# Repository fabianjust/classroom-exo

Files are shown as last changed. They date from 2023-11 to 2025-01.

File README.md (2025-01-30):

# classroom-exo
Classroom-ready open-source educational exoskeleton for biomedical and control engineering

The classroom Exo development is guided by the manual.
The manual is designed to assist you in seamlessly transitioning from EduExoPro to Classroom Exo. Whether you're a developer, educator, or enthusiast, the detailed content in each folder aims to provide clarity and guidance.

How to Use This Manual:
Begin by reading through the manual to familiarize yourself with the upgrade process.
Depending on your area of interest or expertise, navigate to the specific folders that match your requirements—whether it's CAD, PCB design, electronics, or material lists.
Feel free to collaborate by providing feedback, raising issues, or contributing to the ongoing development of Classroom Exo. Your input is highly valued.

We prepared three lab instructions for a) Force Control, b) Muscle Activity Control, and c) PID Control for Biomedical and Control Engineering University Education. Feel free to use these documents to build your own lab for a physical human-machine interaction, health robotics, and for all control theory courses.

If you want to know more about the Classroom Exo, check out the corresponding Journal Paper: https://www.degruyter.com/document/doi/10.1515/auto-2023-0208/html

We hope this manual serves as a valuable resource in your journey to implement Classroom Exo. 
Happy exploring and building with Classroom Exo!

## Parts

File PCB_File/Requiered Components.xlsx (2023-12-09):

Reference | Value | MPN | Qty/unit | LINK | Column1
> R2-R4 | 10k | RC0805JR-0710KL | 3 | LINK (https://www.digikey.se/en/products/detail/yageo/RC0805JR-0710KL/728241)
R13 | 300R | RC0805JR-07300RL | 1 | LINK (https://www.digikey.se/en/products/detail/yageo/RC0805JR-07300RL/728307?s=N4IgTCBcDaIEoGEAMAOJBWAUnAtEg7AMxJJwAyIAugL5A)
R1 | 60.4R | RC0805FR-0760R4L | 1 | LINK (https://www.digikey.se/en/products/detail/yageo/RC0805FR-0760R4L/728073)
R11 | 5.24k | RC0805FR-075K23L | 1 | LINK (https://www.digikey.se/en/products/detail/yageo/RC0805FR-075K23L/727993)
R12 | 30.31k | RC0805FR-0730K1L | 1 | LINK (https://www.digikey.se/en/products/detail/yageo/RC0805FR-0730K1L/727845)
> R6, R7 | 100k | RC0805FR-13100KL | 2 | LINK (https://www.digikey.se/en/products/detail/yageo/RC0805FR-13100KL/13694147?s=N4IgTCBcDaIEoGEAMAOJBWAYnAtARgGY8kkBpAGRAF0BfIA)
R8 | 383R | RC0805FR-07383RL | 1 | LINK (https://www.digikey.se/en/products/detail/yageo/RC0805FR-07383RL/727896?s=N4IgTCBcDaIEoGEAMAOJBWAYnAtEg7AMwqFwAyIAugL5A)
R14 | 170R | RC0805FR-07174RL | 1 | LINK (https://www.digikey.se/en/products/detail/yageo/RC0805FR-07174RL/727639)
D3 | LED_RED | LTST-C191KRKT | 1 | LINK (https://www.digikey.se/en/products/detail/liteon/LTST-C191KRKT/386837?s=N4IgTCBcDaIDIBUDKCC0BhAjATkwaQCU8EQBdAXyA)
D2 | LED_Blue | LTST-C191TBKT | 1 | LINK (https://www.digikey.se/en/products/detail/liteon/LTST-C191TBKT/388530)
> D5, D6 | ESD321 | ESD321DPYR | 2 | LINK (https://www.digikey.se/en/products/detail/texas-instruments/ESD321DPYR/9559035?s=N4IgTCBcDaIKIGUAiBmMBGJAFAmgJRAF0BfIA)
D4 | D1213A | D1213A-01WS-7 | 1 | LINK (https://www.digikey.se/en/products/detail/diodes-incorporated/D1213A-01WS-7/3340446?s=N4IgTCBcDaICIEYwIMwEEC0AGBB1AyhgOwgC6AvkA)
C2 | 6.8uF | C2012X8L0J685K125AC | 1 | LINK (https://www.digikey.se/en/products/detail/tdk-corporation/C2012X8L0J685K125AC/8343788)
C4 | 47nF | C2012X7T2W473K125AA | 1 | LINK (https://www.digikey.se/en/products/detail/tdk-corporation/C2012X7T2W473K125AA/2733189)
> C9, C10, C12, C14, C17 | 100nF | C2012X7R2A104K125AA | 5 | LINK (https://www.digikey.se/en/products/detail/tdk-corporation/C2012X7R2A104K125AA/569044?s=N4IgTCBcDaIMJgAwEYwA0DsAlMBBZiALANKoCsuuIAugL5A)
> C1, C11, C13, C15, C18 | 1uF | C2012X7R1H105K125AB | 5 | LINK (https://www.digikey.se/en/products/detail/tdk-corporation/C2012X7R1H105K125AB/2732982)
> C7, C8 | 22uF | C2012X5R1V226M125AC | 2 | LINK (https://www.digikey.se/en/products/detail/tdk-corporation/C2012X5R1V226M125AC/3951664?s=N4IgTCBcDaIMJgAwEYwA0CsAlZA1MYAbALKoYCCcIAugL5A)
C5 | 4.7uF | C2012X5R1E475K125AB | 1 | LINK (https://www.digikey.se/en/products/detail/tdk-corporation/C2012X5R1E475K125AB/1986842)
> C3, C6, C16 | 10uF | C2012X5R1E106K125AB | 3 | LINK (https://www.digikey.se/en/products/detail/tdk-corporation/C2012X5R1E106K125AB/2443462)
D1 | BAT60B | BAT60BE6327HTSA1 | 1 | LINK (https://www.digikey.se/en/products/detail/infineon-technologies/BAT60BE6327HTSA1/1280935)
J5 | USB_B_Micro | 10118192-0002LF | 1 | LINK (https://www.digikey.se/en/products/detail/amphenol-cs-fci/10118192-0002LF/6817756?s=N4IgTCBcDaIIwAY5wBxwJxgLQN2AMgGIgC6AvkA)
J4 | SRV0 | 1-2834011-4 | 1 | LINK (https://www.digikey.se/en/products/detail/te-connectivity-amp-connectors/1-2834011-4/5872966?s=N4IgTCBcDaIIwFowA4DMAWADHR6QF0BfIA)
J3 | SG0 | 1-2834011-4 | 1 | LINK (https://www.digikey.se/en/products/detail/te-connectivity-amp-connectors/1-2834011-4/5872966?s=N4IgTCBcDaIIwFowA4DMAWADHR6QF0BfIA)
J2 | EMG1 | 1-2834011-3 | 1 | LINK (https://www.digikey.se/en/products/detail/te-connectivity-amp-connectors/1-2834011-3/5872965?s=N4IgTCBcDaIIwFowA4DMAWADHRqQF0BfIA)
J1 | EMG0 | 1-2834011-3 | 1 | LINK (https://www.digikey.se/en/products/detail/te-connectivity-amp-connectors/1-2834011-3/5872965?s=N4IgTCBcDaIIwFowA4DMAWADHRqQF0BfIA)
J6 | BAT0 | 1-2834011-2 | 1 | LINK (https://www.digikey.se/en/products/detail/te-connectivity-amp-connectors/1-2834011-2/5872964?s=N4IgTCBcDaIIwFowA4DMAWADHREC6AvkA)
L1 | 1uH | 0630CDMCCDS-1R5MC | 1 | LINK (https://www.digikey.se/en/products/detail/sumida-america-inc/0630CDMCCDS-1R5MC/5812455)
U3 (RGBSwitch) | LP11EE1NCSRGB | LP11EE1NCSRGB | 1 | LINK (https://www.digikey.se/en/products/detail/e-switch/LP11EE1NCSRGB/9771933?s=N4IgTCBcDaIDIAUCMSCiqkDkDCBlASgOIBCIAugL5A)
U2 (BatteryManagment) | BQ25886RGER | BQ25886RGER | 1 | LINK (https://www.digikey.se/en/products/detail/texas-instruments/BQ25886RGER/10273215?s=N4IgTCBcDaIEIEUwFYAcqBsAlA4gUSxAF0BfIA)
U1 (Amplifier) | INA125P | INA125P | 3 | LINK (https://www.digikey.se/en/products/detail/texas-instruments/INA125P/254670)
U1 (Socket) | INA125P | ICM-316-1-GT-HT | 3 | LINK (https://www.digikey.se/en/products/detail/adam-tech/ICM-316-1-GT-HT/9833008?s=N4IgTCBcDaIJIGECyBaAzARgGwoyg4gCooAShIAugL5A)
R10 | Iset (5.7k) | RC0805FR-075K76L | 1 | LINK (https://www.digikey.se/en/products/detail/yageo/RC0805FR-075K76L/728007)
R9 | Vset(150k) | RC0805FR-07150KL | 1 | LINK (https://www.digikey.se/en/products/detail/yageo/RC0805FR-07150KL/727614)
Q2 | Si3483CDV | SI3483CDV-T1-GE3 | 1 | LINK (https://www.digikey.se/en/products/detail/vishay-siliconix/SI3483CDV-T1-GE3/2441608)
Q1 | BSS123 | BSS123 | 1 | LINK (https://www.digikey.se/en/products/detail/anbon-semiconductor-int-l-limited/BSS123/16708487)
A1 | Arduino_Nano_33_IOT | PPPC101LFBN-RC (10P) | 2 | LINK (https://www.digikey.se/en/products/detail/sullins-connector-solutions/PPPC101LFBN-RC/810182?s=N4IgTCBcDaIAoIMIEYAMyAyAxAQgOQFoAlREAXQF8g)
A1 | Arduino_Nano_33_IOT | PPPC051LFBN-RC (5P) | 2 | LINK (https://www.digikey.se/en/products/detail/sullins-connector-solutions/PPPC051LFBN-RC/810177?s=N4IgTCBcDaIAoIMIAYCsBGAMgMQEIDkBaAJURAF0BfIA)
PWR_TP | TestPoint (White) | 5000 | 6 | LINK (https://www.digikey.se/en/products/detail/keystone-electronics/5000/255326)
SRV0_TP | TestPoint (Yellow) | 5004 | 4 | LINK (https://www.digikey.se/en/products/detail/keystone-electronics/5004/362669)
> EMG0, EMG1_TP | TestPoint (Orange) | 5003 | 2 | LINK (https://www.digikey.se/en/products/detail/keystone-electronics/5003/362668)
> GND_TP | TestPoint (Black) | 5001 | 4 | LINK (https://www.digikey.se/en/products/detail/keystone-electronics/5001/255327)
SG0_TP | TestPoint (White) | 5002 | 3 | LINK (https://www.digikey.se/en/products/detail/keystone-electronics/5002/255328)
Myoware Cable | Myoware Cable | CAB-12970 | 2 | LINK (https://www.digikey.se/sv/products/detail/sparkfun-electronics/CAB-12970/6833933?productid=6833933)
Myoware Cable Shield | Myoware Cable Shield | Myoware Cable Shield | 2 | LINK (https://www.fruugo.se/replacement-wearable-for-myoware-cable-shield-muscle-sensor-module-board/p-118668884-249379639?language=en&ac=ProductCasterAPI&asc=pmax)
Screw thread Insert M3 |  | K0978.03 | 15 | Link (https://uk.misumi-ec.com/vona2/detail/221303964730/?HissuCode=K0978.03)
Screw thread Insert M4 |  | K0978.04 | 15 | link (https://uk.misumi-ec.com/vona2/detail/221303964730/?HissuCode=K0978.04)
Screw M3 |  | S3-6-P | 15 | Link (https://uk.misumi-ec.com/vona2/detail/221005514842/?HissuCode=S3-6-P)
Screw M4 |  | S4-45-P | 15 | link (https://uk.misumi-ec.com/vona2/detail/221005514842/?HissuCode=S4-45-P)
Battery | 7.4V/8.4V | CL-LP503759-2S1P |  | Link (https://www.batteriexperten.com/sv/artiklar/li-po-2s-74v-30c-1300mah-jst-rcy-bec-kontakt-vapex.html)
Soldering | NC191LT10 | NC191LT10
SRA NO CLEAN PASTE FLUX | FLS135NC | FLS135NC
 |  |  |  |  |  | # The quantities provided in this list represent the minimum requirement. We strongly recommend acquiring a surplus of components beyond the specified quantities for added flexibility and contingencies.

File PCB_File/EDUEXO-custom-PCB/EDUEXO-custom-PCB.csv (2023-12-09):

Source: | C:\Users\Mohammed Al-Tashi\Desktop\EXO V2\PCB_Designs\EDUEXO-custom-PCB\EDUEXO-custom-PCB.kicad_sch
Date: | 5/17/2023 20:34
Tool: | Eeschema (6.0.5)
Generator: | C:\Program Files\KiCad\6.0\bin\scripting\plugins/bom_csv_grouped_by_value.py
Component Count: | 74
Individual Components:
Item | Qty | Reference(s) | Value | LibPart | Footprint | Datasheet | MPN | config
 |  | +3V3 | TestPoint | Connector:TestPoint | TestPoint:TestPoint_Keystone_5000-5004_Miniature | https://www.keyelco.com/userAssets/file/M65p56.pdf | 5002
 |  | +5V0 | TestPoint | Connector:TestPoint | TestPoint:TestPoint_Keystone_5000-5004_Miniature | https://www.keyelco.com/userAssets/file/M65p56.pdf | 5002
 |  | A1 | Arduino_Nano_33_IOT | EDUEXO-custom-PCB:Arduino_Nano_33_IOT | EDUEXO-custom-PCB:MODULE_ABX00027_ThroughHoles | https://docs.arduino.cc/resources/datasheets/ABX00027-datasheet.pdf
 |  | ANGLE_SRV0 | TestPoint | Connector:TestPoint | TestPoint:TestPoint_Keystone_5000-5004_Miniature | https://www.keyelco.com/userAssets/file/M65p56.pdf | 5002
 |  | ARDu_CONTROL_SRV0 | TestPoint | Connector:TestPoint | TestPoint:TestPoint_Keystone_5000-5004_Miniature | https://www.keyelco.com/userAssets/file/M65p56.pdf | 5002
 |  | BAT_VALUE_0 | TestPoint | Connector:TestPoint | TestPoint:TestPoint_Keystone_5000-5004_Miniature | https://www.keyelco.com/userAssets/file/M65p56.pdf | 5002
 |  | C1 | 1uF | Device:C | Capacitor_SMD:C_0805_2012Metric | https://product.tdk.com/en/system/files | C2012X7R1H105K125AB
 |  | C2 | 6.8uF | Device:C | Capacitor_SMD:C_0805_2012Metric | https://product.tdk.com/en/system/files | C2012X8L0J685K125AC
 |  | C3 | 10uF | Device:C | Capacitor_SMD:C_0805_2012Metric | https://product.tdk.com/system/files/dam/doc/product/capacitor/ceramic/mlcc/catalog/mlcc_commercial_general_en.pdf | C2012X5R1E106K125AB
 |  | C4 | 47nF | Device:C | Capacitor_SMD:C_0805_2012Metric | https://product.tdk.com/en/system/files | C2012X7T2W473K125AA
 |  | C5 | 4.7uF | Device:C | Capacitor_SMD:C_0805_2012Metric | https://product.tdk.com/system/files/dam/doc/product/capacitor/ceramic/mlcc/catalog/mlcc_commercial_general_en.pdf | C2012X5R1E475K125AB
 |  | C6 | 10uF | Device:C | Capacitor_SMD:C_0805_2012Metric | https://product.tdk.com/system/files/dam/doc/product/capacitor/ceramic/mlcc/catalog/mlcc_commercial_general_en.pdf | C2012X5R1E106K125AB
 |  | C7 | 22uF | Device:C | Capacitor_SMD:C_0805_2012Metric | https://product.tdk.com/system/files/dam/doc/product/capacitor/ceramic/mlcc/catalog/mlcc_commercial_general_en.pdf | C2012X5R1V226M125AC
 |  | C8 | 22uF | Device:C | Capacitor_SMD:C_0805_2012Metric | https://product.tdk.com/system/files/dam/doc/product/capacitor/ceramic/mlcc/catalog/mlcc_commercial_general_en.pdf | C2012X5R1V226M125AC
 |  | C9 | 100nF | Device:C | Capacitor_SMD:C_0805_2012Metric | https://product.tdk.com/en/system/files | C2012X7R2A104K125AA
 |  | C10 | 100nF | Device:C | Capacitor_SMD:C_0805_2012Metric | https://product.tdk.com/en/system/files | C2012X7R2A104K125AA
 |  | C11 | 1uF | Device:C | Capacitor_SMD:C_0805_2012Metric | https://product.tdk.com/en/system/files | C2012X7R1H105K125AB
 |  | C12 | 100nF | Device:C | Capacitor_SMD:C_0805_2012Metric | https://product.tdk.com/en/system/files | C2012X7R2A104K125AA
 |  | C13 | 1uF | Device:C | Capacitor_SMD:C_0805_2012Metric | https://product.tdk.com/en/system/files | C2012X7R1H105K125AB
 |  | C14 | 100nF | Device:C | Capacitor_SMD:C_0805_2012Metric | https://product.tdk.com/en/system/files | C2012X7R2A104K125AA
 |  | C15 | 1uF | Device:C | Capacitor_SMD:C_0805_2012Metric | https://product.tdk.com/en/system/files | C2012X7R1H105K125AB
 |  | C16 | 10uF | Device:C | Capacitor_SMD:C_0805_2012Metric | https://product.tdk.com/system/files/dam/doc/product/capacitor/ceramic/mlcc/catalog/mlcc_commercial_general_en.pdf | C2012X5R1E106K125AB
 |  | C17 | 100nF | Device:C | Capacitor_SMD:C_0805_2012Metric | https://product.tdk.com/en/system/files | C2012X7R2A104K125AA
 |  | C18 | 1uF | Device:C | Capacitor_SMD:C_0805_2012Metric | https://product.tdk.com/en/system/files | C2012X7R1H105K125AB
 |  | D1 | BAT60B | Device:D_Schottky | Diode_SMD:D_SOD-323 | https://www.infineon.com/dgdl/bat60bseries.pdf?folderId=db3a304313d846880113def5812204a1&fileId=db3a304314dca3890115195908c50f0b | BAT60BE6327HTSA1
 |  | D2 | LED_Blue | Device:LED | LED_SMD:LED_0603_1608Metric | https://optoelectronics.liteon.com/upload/download/DS22-2000-230/LTST-C191TBKT.pdf | LTST-C191TBKT
 |  | D3 | LED_RED | Device:LED | LED_SMD:LED_0603_1608Metric | https://optoelectronics.liteon.com/upload/download/DS22-2000-223/LTST-C191KRKT.PDF | LTST-C191KRKT
 |  | D4 | D1213A | Device:D_Zener | Diode_SMD:D_SOD-323 | https://www.diodes.com/assets/Datasheets/D1213A-01WS.pdf | D1213A-01WS-7
 |  | D5 | ESD321 | Diode:ESD9B3.3ST5G | Diode_SMD:D_0402_1005Metric | https://www.ti.com/lit/ds/symlink/esd321.pdf?HQS=dis-dk-null-digikeymode-dsf-pf-null-wwe&ts=1683194956063 | ESD321DPYR
 |  | D6 | ESD321 | Diode:ESD9B3.3ST5G | Diode_SMD:D_0402_1005Metric | https://www.ti.com/lit/ds/symlink/esd321.pdf?HQS=dis-dk-null-digikeymode-dsf-pf-null-wwe&ts=1683194956063 | ESD321DPYR
 |  | DRIVE_PWM_SRV0 | TestPoint | Connector:TestPoint | TestPoint:TestPoint_Keystone_5000-5004_Miniature | https://www.keyelco.com/userAssets/file/M65p56.pdf | 5002
 |  | EMG0 | TestPoint | Connector:TestPoint | TestPoint:TestPoint_Keystone_5000-5004_Miniature | https://www.keyelco.com/userAssets/file/M65p56.pdf | 5002
 |  | EMG1 | TestPoint | Connector:TestPoint | TestPoint:TestPoint_Keystone_5000-5004_Miniature | https://www.keyelco.com/userAssets/file/M65p56.pdf | 5002
 |  | GND1 | TestPoint | Connector:TestPoint | TestPoint:TestPoint_Keystone_5000-5004_Miniature | https://www.keyelco.com/userAssets/file/M65p56.pdf | 5002
 |  | GND2 | TestPoint | Connector:TestPoint | TestPoint:TestPoint_Keystone_5000-5004_Miniature | https://www.keyelco.com/userAssets/file/M65p56.pdf | 5002
 |  | GND3 | TestPoint | Connector:TestPoint | TestPoint:TestPoint_Keystone_5000-5004_Miniature | https://www.keyelco.com/userAssets/file/M65p56.pdf | 5002
 |  | GND4 | TestPoint | Connector:TestPoint | TestPoint:TestPoint_Keystone_5000-5004_Miniature | https://www.keyelco.com/userAssets/file/M65p56.pdf | 5002
 |  | H1 | M3 | Mechanical:MountingHole | MountingHole:MountingHole_3.2mm_M3 | ~
 |  | H2 | M3 | Mechanical:MountingHole | MountingHole:MountingHole_3.2mm_M3 | ~
 |  | H3 | M3 | Mechanical:MountingHole | MountingHole:MountingHole_3.2mm_M3 | ~
 |  | H4 | M3 | Mechanical:MountingHole | MountingHole:MountingHole_3.2mm_M3 | ~
 |  | J1 | EMG0 | Connector:Screw_Terminal_01x03 | EDUEXO-custom-PCB:TE_1-2834011-3 | https://www.te.com/commerce/DocumentDelivery/DDEController?Action=srchrtrv&DocNm=1-1773872-7_ModularScrewlessTerminalBloc&DocType=DS&DocLang=English | 1-2834011-3
 |  | J2 | EMG1 | Connector:Screw_Terminal_01x03 | EDUEXO-custom-PCB:TE_1-2834011-3 | https://www.te.com/commerce/DocumentDelivery/DDEController?Action=srchrtrv&DocNm=1-1773872-7_ModularScrewlessTerminalBloc&DocType=DS&DocLang=English | 1-2834011-3
 |  | J3 | SG0 | Connector:Screw_Terminal_01x04 | EDUEXO-custom-PCB:TE_1-2834011-4 | https://www.te.com/commerce/DocumentDelivery/DDEController?Action=srchrtrv&DocNm=1-1773872-7_ModularScrewlessTerminalBloc&DocType=DS&DocLang=English | 1-2834011-4
 |  | J4 | SRV0 | Connector:Screw_Terminal_01x04 | EDUEXO-custom-PCB:TE_1-2834011-4 | https://www.te.com/commerce/DocumentDelivery/DDEController?Action=srchrtrv&DocNm=2834011&DocType=Customer+Drawing&DocLang=English | 1-2834011-4
 |  | J5 | USB_B_Micro | EDUEXO-custom-PCB:USB_B_Micro | EDUEXO-custom-PCB:USB_micro_B_10118192-0002LF | https://www.amphenol-cs.com/media/wysiwyg/files/drawing/10118192.pdf | 10118192-0002LF
 |  | J6 | BAT0 | Connector:Screw_Terminal_01x02 | EDUEXO-custom-PCB:TE_1-2834011-2 | https://www.te.com/commerce/DocumentDelivery/DDEController?Action=srchrtrv&DocNm=2834011&DocType=Customer+Drawing&DocLang=English | 1-2834011-2
 |  | L1 | 1uH | pspice:INDUCTOR | EDUEXO-custom-PCB:L_0630CDMCCDS-1R5MC | https://products.sumida.com/products/pdf/0630CDMCCDS.pdf?t=1611592302 | 0630CDMCCDS-1R5MC
 |  | OUTPUT_SG0 | TestPoint | Connector:TestPoint | TestPoint:TestPoint_Keystone_5000-5004_Miniature | https://www.keyelco.com/userAssets/file/M65p56.pdf | 5002
 |  | POWER_SRV0 | TestPoint | Connector:TestPoint | TestPoint:TestPoint_Keystone_5000-5004_Miniature | https://www.keyelco.com/userAssets/file/M65p56.pdf | 5002
 |  | Q1 | BSS123 | Transistor_FET:BSS123 | Package_TO_SOT_SMD:SOT-23 | http://www.diodes.com/assets/Datasheets/ds30366.pdf
 |  | Q2 | Si3483CDV | EDUEXO-custom-PCB:Si3483CDV | Package_TO_SOT_SMD:TSOT-23-6 | https://www.vishay.com/docs/68603/si3483cd.pdf
 |  | R1 | 60.4R | Device:R | Resistor_SMD:R_0805_2012Metric | https://www.yageo.com/upload/media/product/productsearch/datasheet/rchip/PYu-RC_Group_51_RoHS_L_12.pdf | RC0805FR-0760R4L
 |  | R2 | 10k | Device:R | Resistor_SMD:R_0805_2012Metric | https://www.yageo.com/upload/media/product/productsearch/datasheet/rchip/PYu-RC_Group_51_RoHS_L_12.pdf | RC0805JR-0710KL
 |  | R3 | 10k | Device:R | Resistor_SMD:R_0805_2012Metric | https://www.yageo.com/upload/media/product/productsearch/datasheet/rchip/PYu-RC_Group_51_RoHS_L_12.pdf | RC0805JR-0710KL
 |  | R4 | 10k | Device:R | Resistor_SMD:R_0805_2012Metric | https://www.yageo.com/upload/media/product/productsearch/datasheet/rchip/PYu-RC_Group_51_RoHS_L_12.pdf | RC0805JR-0710KL
 |  | R6 | 100k | Device:R | Resistor_SMD:R_0805_2012Metric | https://www.yageo.com/upload/media/product/productsearch/datasheet/rchip/PYu-RC_Group_51_RoHS_L_12.pdf | RC0805FR-13100KL
 |  | R7 | 100k | Device:R | Resistor_SMD:R_0805_2012Metric | https://www.yageo.com/upload/media/product/productsearch/datasheet/rchip/PYu-RC_Group_51_RoHS_L_12.pdf | RC0805FR-13100KL
 |  | R8 | 383R | Device:R | Resistor_SMD:R_0805_2012Metric | https://www.yageo.com/upload/media/product/productsearch/datasheet/rchip/PYu-RC_Group_51_RoHS_L_12.pdf | RC0805FR-07383RL
 |  | R9 | Vset | Device:R | Resistor_SMD:R_0805_2012Metric | https://www.yageo.com/upload/media/product/productsearch/datasheet/rchip/PYu-RC_Group_51_RoHS_L_12.pdf |  | dnf
 |  | R10 | Iset | Device:R | Resistor_SMD:R_0805_2012Metric | https://www.yageo.com/upload/media/product/productsearch/datasheet/rchip/PYu-RC_Group_51_RoHS_L_12.pdf |  | dnf
 |  | R11 | 5.24k | Device:R | Resistor_SMD:R_0805_2012Metric | https://www.yageo.com/upload/media/product/productsearch/datasheet/rchip/PYu-RC_Group_51_RoHS_L_12.pdf | RC0805FR-075K23L
 |  | R12 | 30.31k | Device:R | Resistor_SMD:R_0805_2012Metric | https://www.yageo.com/upload/media/product/productsearch/datasheet/rchip/PYu-RC_Group_51_RoHS_L_12.pdf | RC0805FR-0730K1L
 |  | R13 | 300 | Device:R | Resistor_SMD:R_0805_2012Metric | https://www.yageo.com/upload/media/product/productsearch/datasheet/rchip/PYu-RC_Group_51_RoHS_L_12.pdf | RC0805JR-07300RL
 |  | R14 | 170 | Device:R | Resistor_SMD:R_0805_2012Metric | https://www.yageo.com/upload/media/product/productsearch/datasheet/rchip/PYu-RC_Group_51_RoHS_L_12.pdf | RC0805FR-07174RL
 |  | SG0_SGN0 | TestPoint | Connector:TestPoint | TestPoint:TestPoint_Keystone_5000-5004_Miniature | https://www.keyelco.com/userAssets/file/M65p56.pdf | 5002
 |  | SG0_SGN1 | TestPoint | Connector:TestPoint | TestPoint:TestPoint_Keystone_5000-5004_Miniature | https://www.keyelco.com/userAssets/file/M65p56.pdf | 5002
 |  | TH1 | Thermistor_NTC | Device:Thermistor_NTC | Resistor_SMD:R_0805_2012Metric | ~ |  | dnf
 |  | U1 | INA125P | EDUEXO-custom-PCB:INA125P | DIP794W45P254L1969H508Q16 | https://www.ti.com/lit/ds/symlink/ina125.pdf
 |  | U2 | BQ25886RGER | EDUEXO-custom-PCB:BQ25886RGER | EDUEXO-custom-PCB:Texas_S-PVQFN-N24_EP2.1x2.1mm_ThermalVias | https://www.ti.com/lit/ds/symlink/bq25886.pdf?ts=1681211335919
 |  | U3 | LP11EE1NCSRGB | EDUEXO-custom-PCB:LP11EE1NCSRGB | EDUEXO-custom-PCB:SW_LP11EE1NCSRGB | https://sten-eswitch-13110800-production.s3.amazonaws.com/system/asset/product_line/data_sheet/38/LP11.pdf
 |  | VBUS0 | TestPoint | Connector:TestPoint | TestPoint:TestPoint_Keystone_5000-5004_Miniature | https://www.keyelco.com/userAssets/file/M65p56.pdf | 5002
 |  | VDC0 | TestPoint | Connector:TestPoint | TestPoint:TestPoint_Keystone_5000-5004_Miniature | https://www.keyelco.com/userAssets/file/M65p56.pdf | 5002
 |  | VREGN0 | TestPoint | Connector:TestPoint | TestPoint:TestPoint_Keystone_5000-5004_Miniature | https://www.keyelco.com/userAssets/file/M65p56.pdf | 5002
Collated Components:
Item | Qty | Reference(s) | Value | LibPart | Footprint | Datasheet | MPN | config
1 | 19 | +3V3, +5V0, ANGLE_SRV0, ARDu_CONTROL_SRV0, BAT_VALUE_0, DRIVE_PWM_SRV0, EMG0, EMG1, GND1, GND2, GND3, GND4, OUTPUT_SG0, POWER_SRV0, SG0_SGN0, SG0_SGN1, VBUS0, VDC0, VREGN0 | TestPoint | Connector:TestPoint | TestPoint:TestPoint_Keystone_5000-5004_Miniature | https://www.keyelco.com/userAssets/file/M65p56.pdf | 5002
2 | 1 | A1 | Arduino_Nano_33_IOT | EDUEXO-custom-PCB:Arduino_Nano_33_IOT | EDUEXO-custom-PCB:MODULE_ABX00027_ThroughHoles | https://docs.arduino.cc/resources/datasheets/ABX00027-datasheet.pdf
3 | 5 | C1, C11, C13, C15, C18 | 1uF | Device:C | Capacitor_SMD:C_0805_2012Metric | https://product.tdk.com/en/system/files | C2012X7R1H105K125AB
4 | 1 | C2 | 6.8uF | Device:C | Capacitor_SMD:C_0805_2012Metric | https://product.tdk.com/en/system/files | C2012X8L0J685K125AC
5 | 3 | C3, C6, C16 | 10uF | Device:C | Capacitor_SMD:C_0805_2012Metric | https://product.tdk.com/system/files/dam/doc/product/capacitor/ceramic/mlcc/catalog/mlcc_commercial_general_en.pdf | C2012X5R1E106K125AB
6 | 1 | C4 | 47nF | Device:C | Capacitor_SMD:C_0805_2012Metric | https://product.tdk.com/en/system/files | C2012X7T2W473K125AA
7 | 1 | C5 | 4.7uF | Device:C | Capacitor_SMD:C_0805_2012Metric | https://product.tdk.com/system/files/dam/doc/product/capacitor/ceramic/mlcc/catalog/mlcc_commercial_general_en.pdf | C2012X5R1E475K125AB
8 | 2 | C7, C8 | 22uF | Device:C | Capacitor_SMD:C_0805_2012Metric | https://product.tdk.com/system/files/dam/doc/product/capacitor/ceramic/mlcc/catalog/mlcc_commercial_general_en.pdf | C2012X5R1V226M125AC
9 | 5 | C9, C10, C12, C14, C17 | 100nF | Device:C | Capacitor_SMD:C_0805_2012Metric | https://product.tdk.com/en/system/files | C2012X7R2A104K125AA
10 | 1 | D1 | BAT60B | Device:D_Schottky | Diode_SMD:D_SOD-323 | https://www.infineon.com/dgdl/bat60bseries.pdf?folderId=db3a304313d846880113def5812204a1&fileId=db3a304314dca3890115195908c50f0b | BAT60BE6327HTSA1
11 | 1 | D2 | LED_Blue | Device:LED | LED_SMD:LED_0603_1608Metric | https://optoelectronics.liteon.com/upload/download/DS22-2000-230/LTST-C191TBKT.pdf | LTST-C191TBKT
12 | 1 | D3 | LED_RED | Device:LED | LED_SMD:LED_0603_1608Metric | https://optoelectronics.liteon.com/upload/download/DS22-2000-223/LTST-C191KRKT.PDF | LTST-C191KRKT
13 | 1 | D4 | D1213A | Device:D_Zener | Diode_SMD:D_SOD-323 | https://www.diodes.com/assets/Datasheets/D1213A-01WS.pdf | D1213A-01WS-7
14 | 2 | D5, D6 | ESD321 | Diode:ESD9B3.3ST5G | Diode_SMD:D_0402_1005Metric | https://www.ti.com/lit/ds/symlink/esd321.pdf?HQS=dis-dk-null-digikeymode-dsf-pf-null-wwe&ts=1683194956063 | ESD321DPYR
15 | 4 | H1, H2, H3, H4 | M3 | Mechanical:MountingHole | MountingHole:MountingHole_3.2mm_M3 | ~
16 | 1 | J1 | EMG0 | Connector:Screw_Terminal_01x03 | EDUEXO-custom-PCB:TE_1-2834011-3 | https://www.te.com/commerce/DocumentDelivery/DDEController?Action=srchrtrv&DocNm=1-1773872-7_ModularScrewlessTerminalBloc&DocType=DS&DocLang=English | 1-2834011-3
17 | 1 | J2 | EMG1 | Connector:Screw_Terminal_01x03 | EDUEXO-custom-PCB:TE_1-2834011-3 | https://www.te.com/commerce/DocumentDelivery/DDEController?Action=srchrtrv&DocNm=1-1773872-7_ModularScrewlessTerminalBloc&DocType=DS&DocLang=English | 1-2834011-3
18 | 1 | J3 | SG0 | Connector:Screw_Terminal_01x04 | EDUEXO-custom-PCB:TE_1-2834011-4 | https://www.te.com/commerce/DocumentDelivery/DDEController?Action=srchrtrv&DocNm=1-1773872-7_ModularScrewlessTerminalBloc&DocType=DS&DocLang=English | 1-2834011-4
19 | 1 | J4 | SRV0 | Connector:Screw_Terminal_01x04 | EDUEXO-custom-PCB:TE_1-2834011-4 | https://www.te.com/commerce/DocumentDelivery/DDEController?Action=srchrtrv&DocNm=2834011&DocType=Customer+Drawing&DocLang=English | 1-2834011-4
20 | 1 | J5 | USB_B_Micro | EDUEXO-custom-PCB:USB_B_Micro | EDUEXO-custom-PCB:USB_micro_B_10118192-0002LF | https://www.amphenol-cs.com/media/wysiwyg/files/drawing/10118192.pdf | 10118192-0002LF
21 | 1 | J6 | BAT0 | Connector:Screw_Terminal_01x02 | EDUEXO-custom-PCB:TE_1-2834011-2 | https://www.te.com/commerce/DocumentDelivery/DDEController?Action=srchrtrv&DocNm=2834011&DocType=Customer+Drawing&DocLang=English | 1-2834011-2
22 | 1 | L1 | 1uH | pspice:INDUCTOR | EDUEXO-custom-PCB:L_0630CDMCCDS-1R5MC | https://products.sumida.com/products/pdf/0630CDMCCDS.pdf?t=1611592302 | 0630CDMCCDS-1R5MC
23 | 1 | Q1 | BSS123 | Transistor_FET:BSS123 | Package_TO_SOT_SMD:SOT-23 | http://www.diodes.com/assets/Datasheets/ds30366.pdf
24 | 1 | Q2 | Si3483CDV | EDUEXO-custom-PCB:Si3483CDV | Package_TO_SOT_SMD:TSOT-23-6 | https://www.vishay.com/docs/68603/si3483cd.pdf
25 | 1 | R1 | 60.4R | Device:R | Resistor_SMD:R_0805_2012Metric | https://www.yageo.com/upload/media/product/productsearch/datasheet/rchip/PYu-RC_Group_51_RoHS_L_12.pdf | RC0805FR-0760R4L
26 | 3 | R2, R3, R4 | 10k | Device:R | Resistor_SMD:R_0805_2012Metric | https://www.yageo.com/upload/media/product/productsearch/datasheet/rchip/PYu-RC_Group_51_RoHS_L_12.pdf | RC0805JR-0710KL
27 | 2 | R6, R7 | 100k | Device:R | Resistor_SMD:R_0805_2012Metric | https://www.yageo.com/upload/media/product/productsearch/datasheet/rchip/PYu-RC_Group_51_RoHS_L_12.pdf | RC0805FR-13100KL
28 | 1 | R8 | 383R | Device:R | Resistor_SMD:R_0805_2012Metric | https://www.yageo.com/upload/media/product/productsearch/datasheet/rchip/PYu-RC_Group_51_RoHS_L_12.pdf | RC0805FR-07383RL
29 | 1 | R9 | Vset | Device:R | Resistor_SMD:R_0805_2012Metric | https://www.yageo.com/upload/media/product/productsearch/datasheet/rchip/PYu-RC_Group_51_RoHS_L_12.pdf |  | dnf
30 | 1 | R10 | Iset | Device:R | Resistor_SMD:R_0805_2012Metric | https://www.yageo.com/upload/media/product/productsearch/datasheet/rchip/PYu-RC_Group_51_RoHS_L_12.pdf |  | dnf
31 | 1 | R11 | 5.24k | Device:R | Resistor_SMD:R_0805_2012Metric | https://www.yageo.com/upload/media/product/productsearch/datasheet/rchip/PYu-RC_Group_51_RoHS_L_12.pdf | RC0805FR-075K23L
32 | 1 | R12 | 30.31k | Device:R | Resistor_SMD:R_0805_2012Metric | https://www.yageo.com/upload/media/product/productsearch/datasheet/rchip/PYu-RC_Group_51_RoHS_L_12.pdf | RC0805FR-0730K1L
33 | 1 | R13 | 300 | Device:R | Resistor_SMD:R_0805_2012Metric | https://www.yageo.com/upload/media/product/productsearch/datasheet/rchip/PYu-RC_Group_51_RoHS_L_12.pdf | RC0805JR-07300RL
34 | 1 | R14 | 170 | Device:R | Resistor_SMD:R_0805_2012Metric | https://www.yageo.com/upload/media/product/productsearch/datasheet/rchip/PYu-RC_Group_51_RoHS_L_12.pdf | RC0805FR-07174RL
35 | 1 | TH1 | Thermistor_NTC | Device:Thermistor_NTC | Resistor_SMD:R_0805_2012Metric | ~ |  | dnf
36 | 1 | U1 | INA125P | EDUEXO-custom-PCB:INA125P | DIP794W45P254L1969H508Q16 | https://www.ti.com/lit/ds/symlink/ina125.pdf
37 | 1 | U2 | BQ25886RGER | EDUEXO-custom-PCB:BQ25886RGER | EDUEXO-custom-PCB:Texas_S-PVQFN-N24_EP2.1x2.1mm_ThermalVias | https://www.ti.com/lit/ds/symlink/bq25886.pdf?ts=1681211335919
38 | 1 | U3 | LP11EE1NCSRGB | EDUEXO-custom-PCB:LP11EE1NCSRGB | EDUEXO-custom-PCB:SW_LP11EE1NCSRGB | https://sten-eswitch-13110800-production.s3.amazonaws.com/system/asset/product_line/data_sheet/38/LP11.pdf

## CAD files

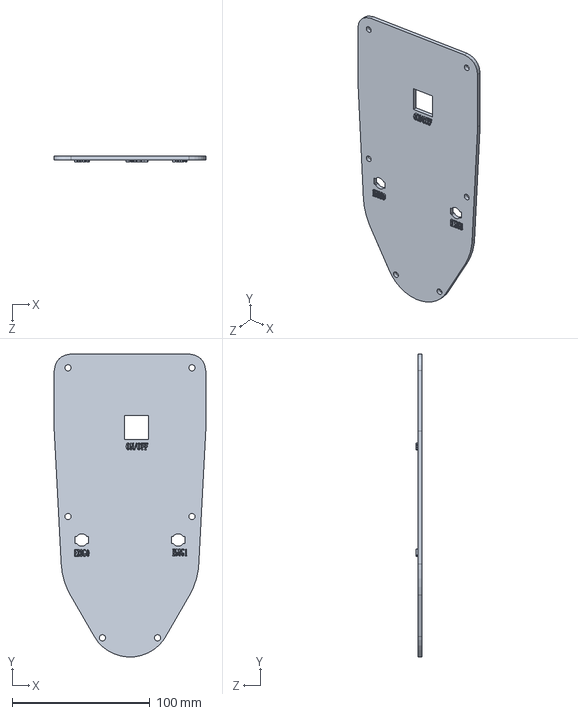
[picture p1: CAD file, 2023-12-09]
CAD_Files/Frontside/3dprint_Editable_File/frontside.SLDPRT
110.0 x 219.9 x 4.20 mm

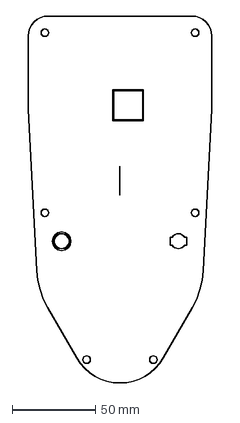
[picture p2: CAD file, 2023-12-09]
CAD_Files/Frontside/LaserCutter/eduexo_frontplate.dxf
110.0 x 220.0 mm

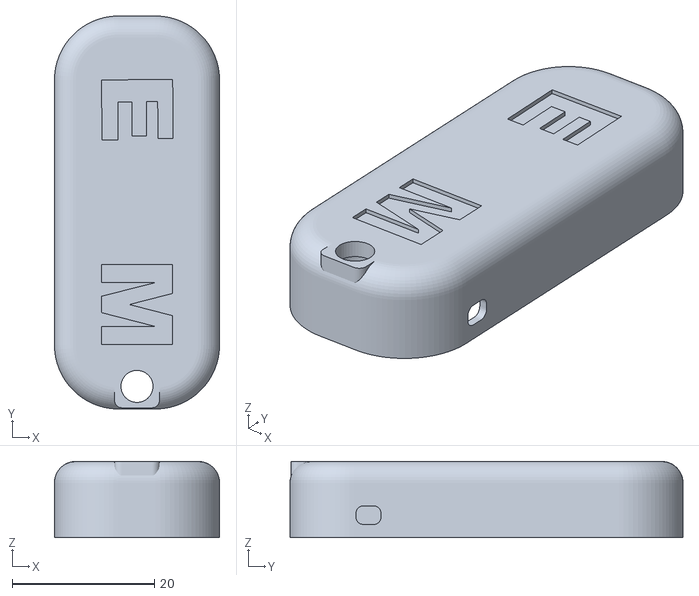
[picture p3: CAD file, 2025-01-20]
CAD_Files/sEMG/Myoware_1.0_Case_V1.stl
23.2 x 55.2 x 10.7

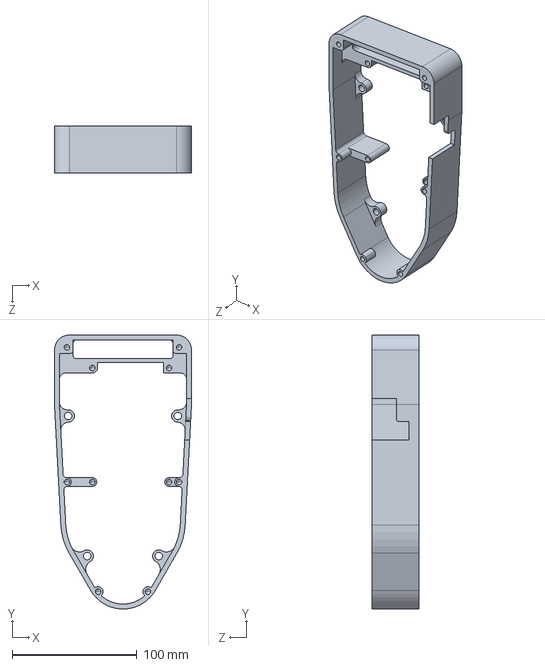
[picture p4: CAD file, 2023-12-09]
CAD_Files/Sidewall/Editable/EduExo_Sidewall_v5.STEP
110.0 x 219.9 x 37.5 mm

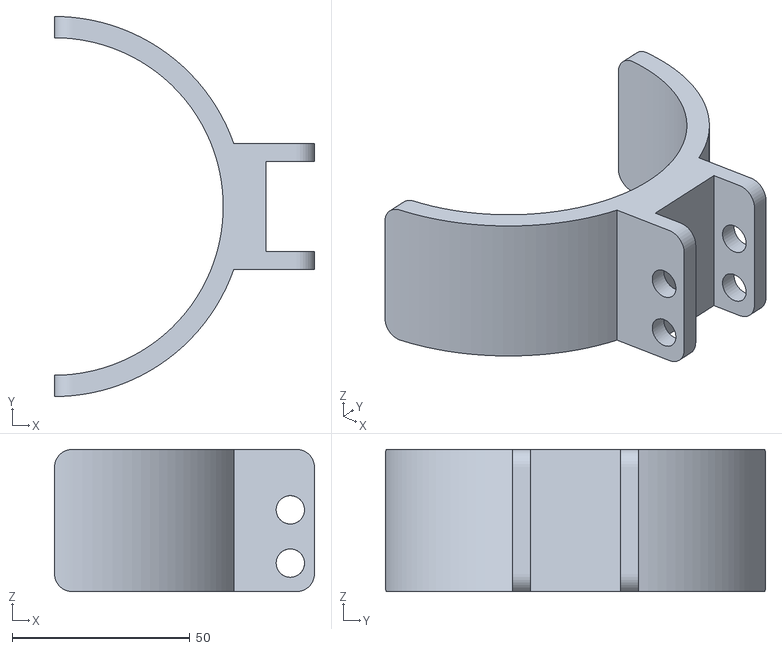
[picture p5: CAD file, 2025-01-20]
CAD_Files/Spare Parts/Wrist_Cuff_v2.stl
73.2 x 107.0 x 40.0

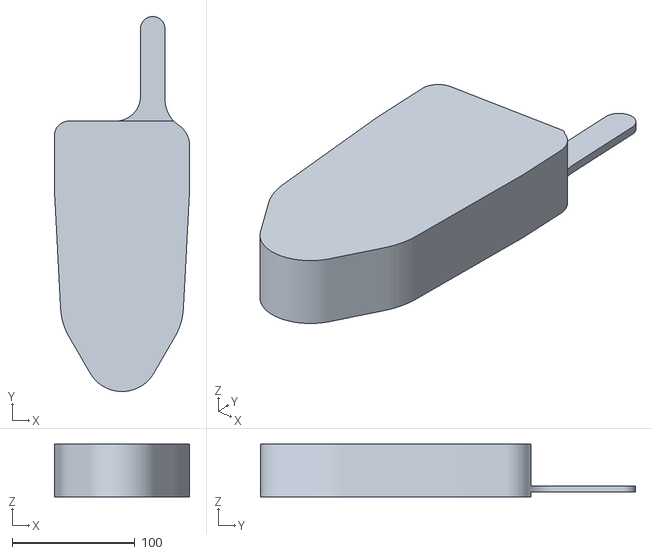
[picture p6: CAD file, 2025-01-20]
Updated BT-GUI_10-24/stl/EduExo_UpperArm v2.stl
110.0 x 305.0 x 43.0

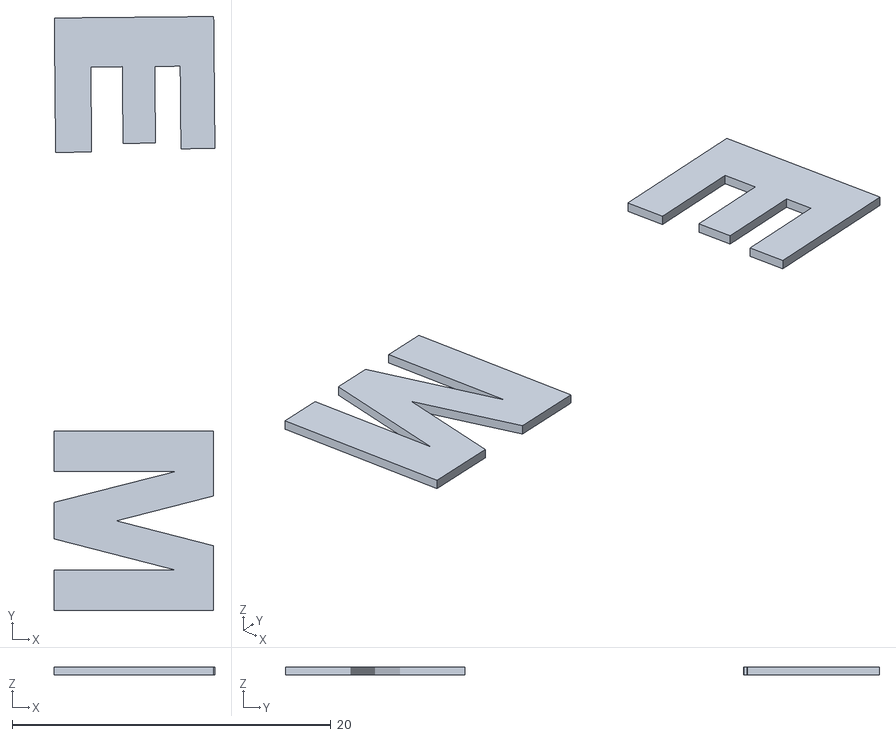
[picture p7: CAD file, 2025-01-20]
CAD_Files/sEMG/Myoware 1.0_Case_V1-letters.stl
10.1 x 37.3 x 0.5

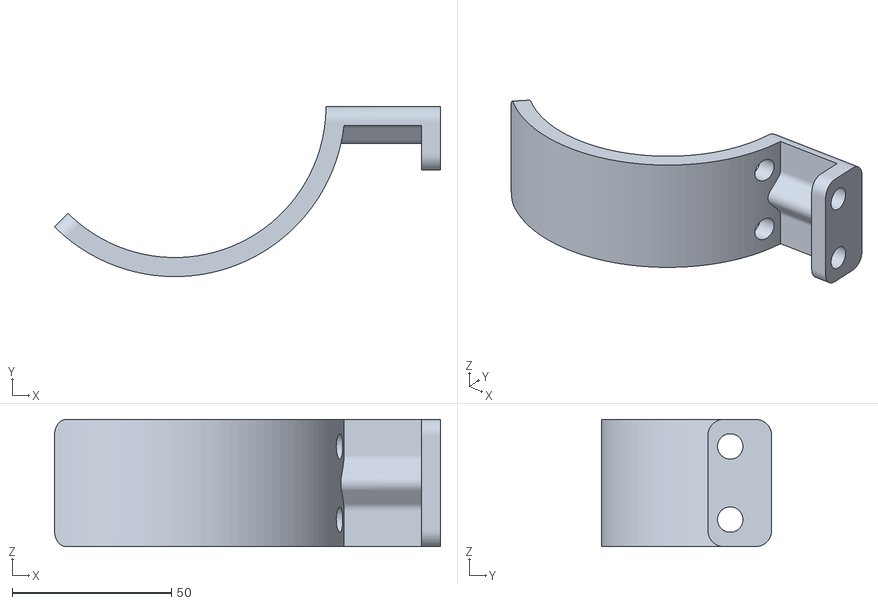
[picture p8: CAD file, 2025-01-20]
CAD_Files/Spare Parts/Cuff_v2.stl
121.3 x 53.5 x 40.0

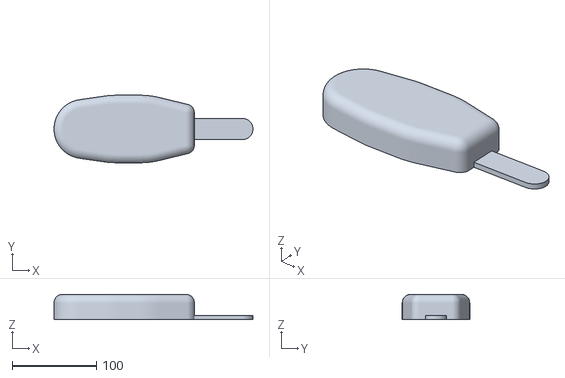
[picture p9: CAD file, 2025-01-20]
Updated BT-GUI_10-24/stl/EduExo_LowerArm v1.stl
235.6 x 80.0 x 30.0

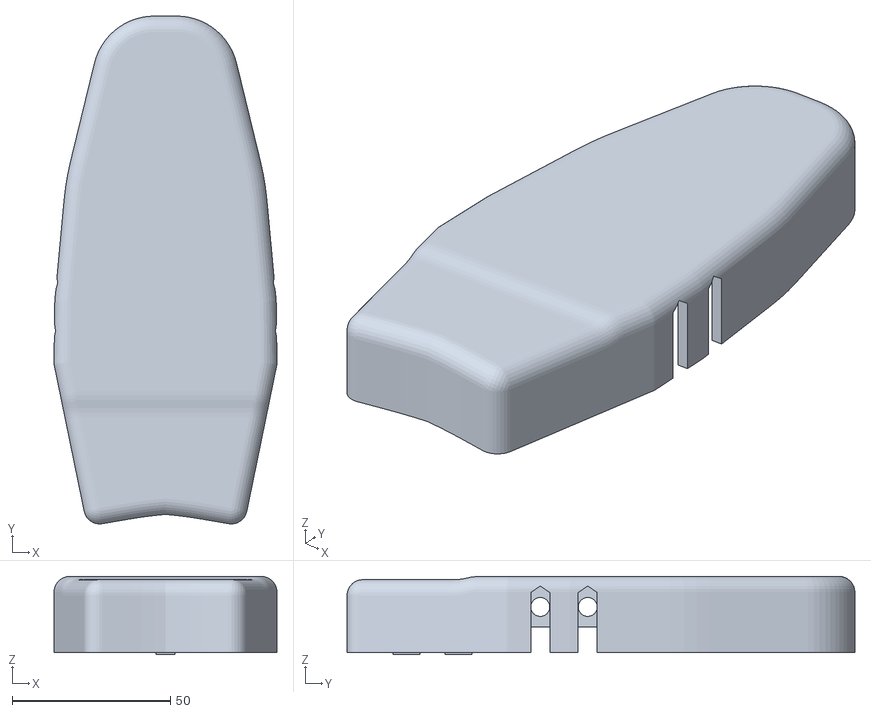
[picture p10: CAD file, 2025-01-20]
CAD_Files/Spare Parts/Wrist_Part_v1.stl
70.5 x 160.5 x 24.7

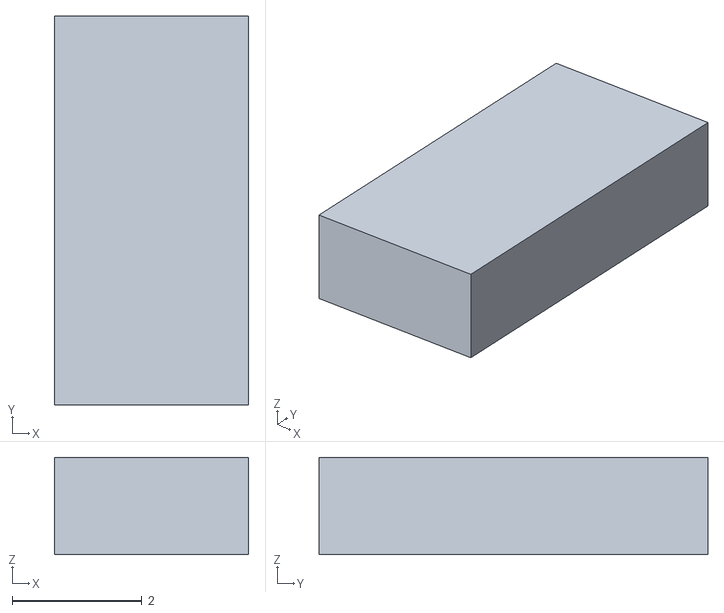
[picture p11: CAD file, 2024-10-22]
Updated BT-GUI_10-24/stl/torso.stl
3.00 x 6.00 x 1.50

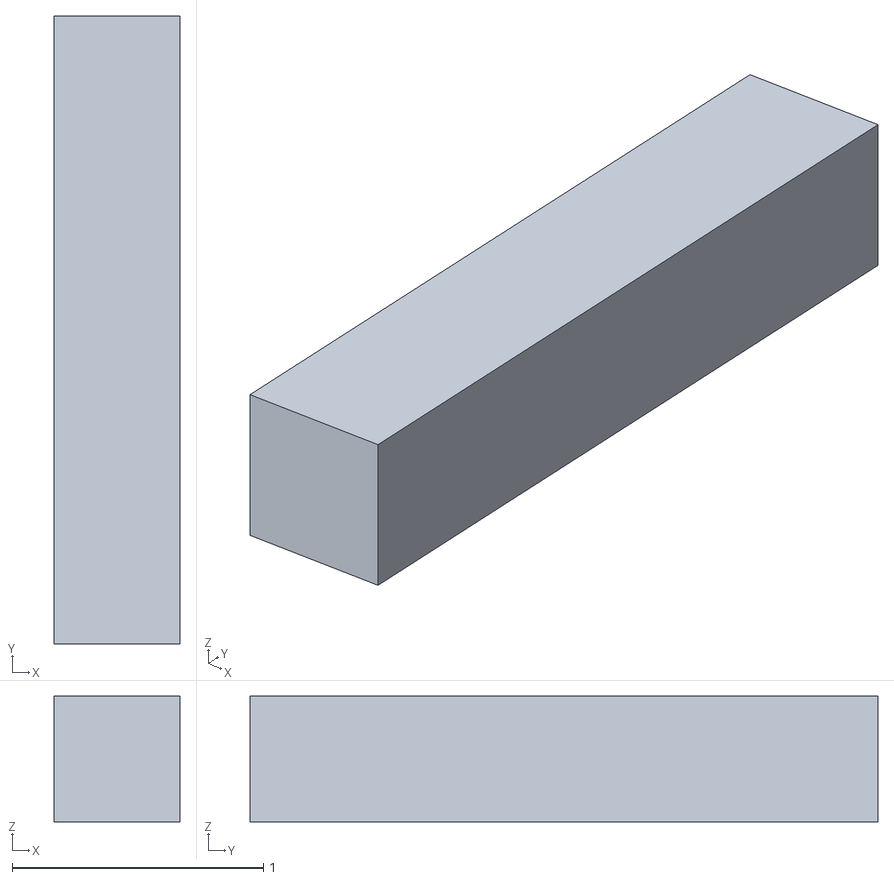
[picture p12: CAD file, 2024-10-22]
Updated BT-GUI_10-24/stl/arm.stl
0.5 x 2.50 x 0.5

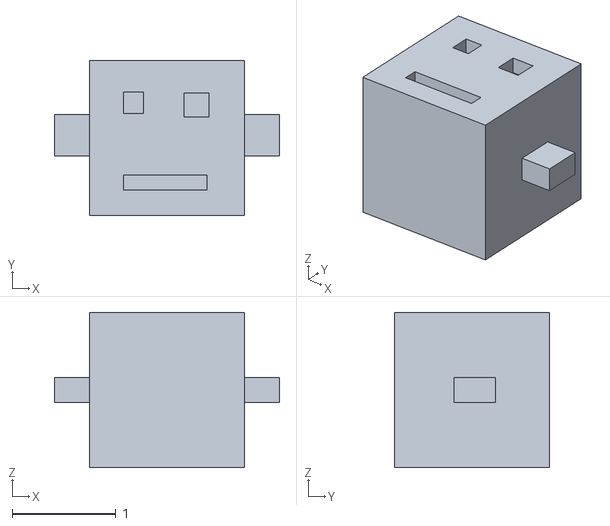
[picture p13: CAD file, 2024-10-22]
Updated BT-GUI_10-24/stl/head.stl
2.17 x 1.50 x 1.50

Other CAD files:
CAD_Files/Sidewall/Editable/EduExo_Sidewall_v5.step.SLDPRT
CAD_Files/Sidewall/Editable/EduExo_Sidewall_v5.STL
Updated BT-GUI_10-24/stl/arm_.stl
Updated BT-GUI_10-24/stl/torso_.stl

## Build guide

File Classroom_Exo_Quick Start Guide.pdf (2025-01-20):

## Chapter 6

# Classroom Exo Quick Start Guide

Summary

This document serves as a quick start quide, to get started with your already assembled Exoskeleton. We will walk you through the necessary MATLAB installation, how to upload the embedded software and how to use the Graphical User Interface (GUI) elements.

## 6.1 Necessary Software and IDEs

The main software components of the Classroom Exo are the embedded software that controls the Exoskeleton’s Hardware, and a Graphical User Interface (GUI) that enables you to interact with all the different functionalities. You will be able to design a pid controller or use the sEMG sensor to control the Motor movement, while adjusting thresholds and other setting easily in MATLAB .Since we are passionate about this Open Source Project, all the files can be accessed on our Github.

To be able to use all the Software you will need to install the following IDEs on you Laptop/PC:

| Arduino IDE
| Mathworks MATLAB (from Version R2023b onward)

Installing the Arduino IDE
Before you can start programming the microcontroller, you have to install the Arduino Integrated Development Environment (IDE). You can download it for several operating systems on the Arduino website: https://www.arduino.cc/. When you install and open the IDE in Figure 6.1a, you will find everything you need to write code and upload it to the Arduino board. To program the Arduino microcontroller, you have to connect it to your computer with a micro-USB cable. You can refer to this link here to get the files to check the servo and sensor using Arduino.

2 | CHAPTER 6. CLASSROOM EXO QUICK START GUIDE

Hint

For more advanced users we recommend using Visual Studio Code with the PlatformIO IDE extension, which offers more advanced debugging options for more complex programs. Please refer to the PlatformIO setup guide here: https://platformio.org/install/ide?install=vscode

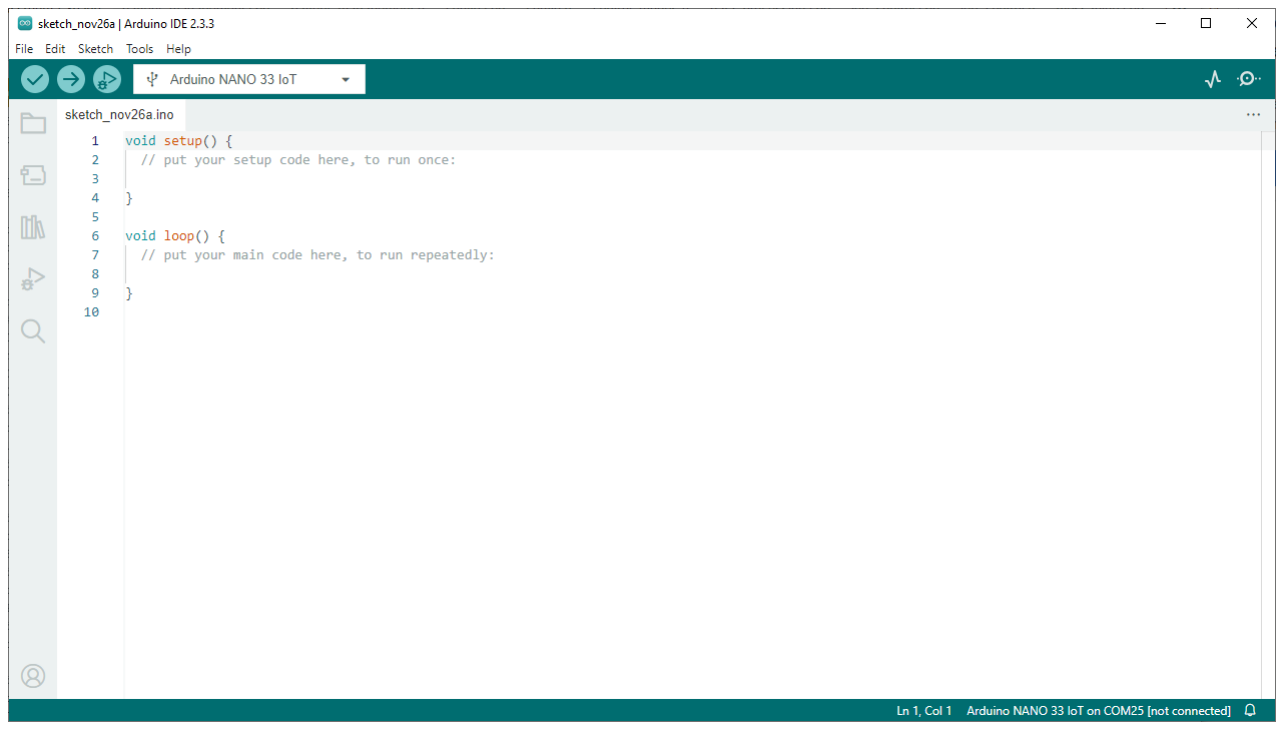
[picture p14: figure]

(a) We use the Arduino IDE for programming all the Components Tests.

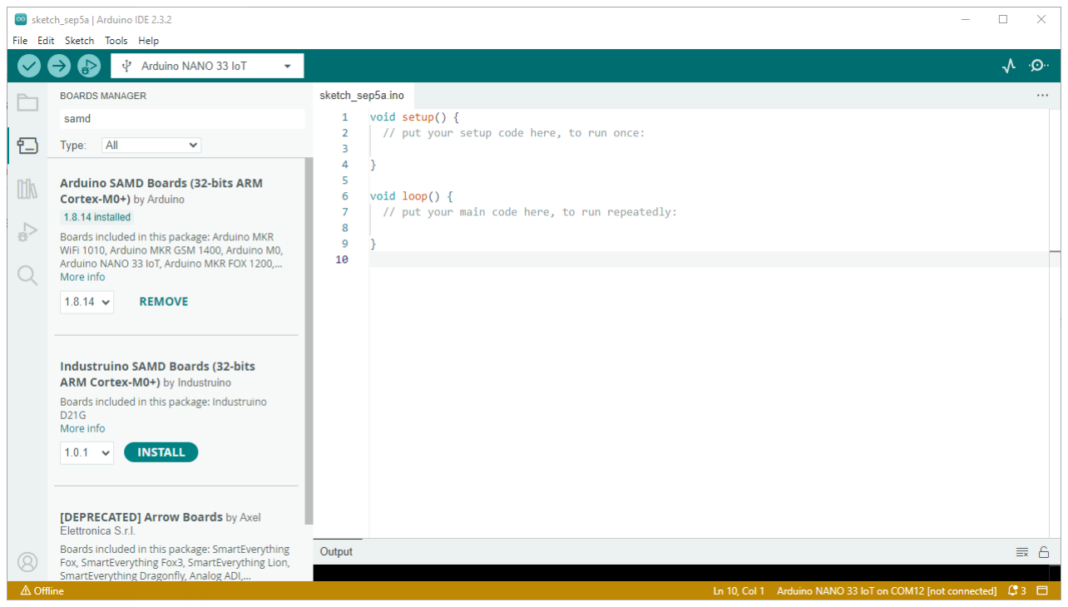
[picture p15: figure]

(b) Make sure to download the correct package for your board.

Figure 6.1: Glimpse of the Arduino IDE and the Board manager

Installing Mathworks MATLAB
Before you can start using the graphical user interface, you will need to install the MATLAB software which is provided by Mathworks. Check with your university to get access to their Mathworks license, create your own Mathworks student account and follow the instructions on their website here: https: //matlab.mathworks.com When you install and open the IDEin Figure 6.2, you will find everything you need to write code in MATLAB. For your ease we have developed a MATLAB GUI, to interact with the Exoskeleton more easily. Refer to our Github repository, in order to get access to the GUI.

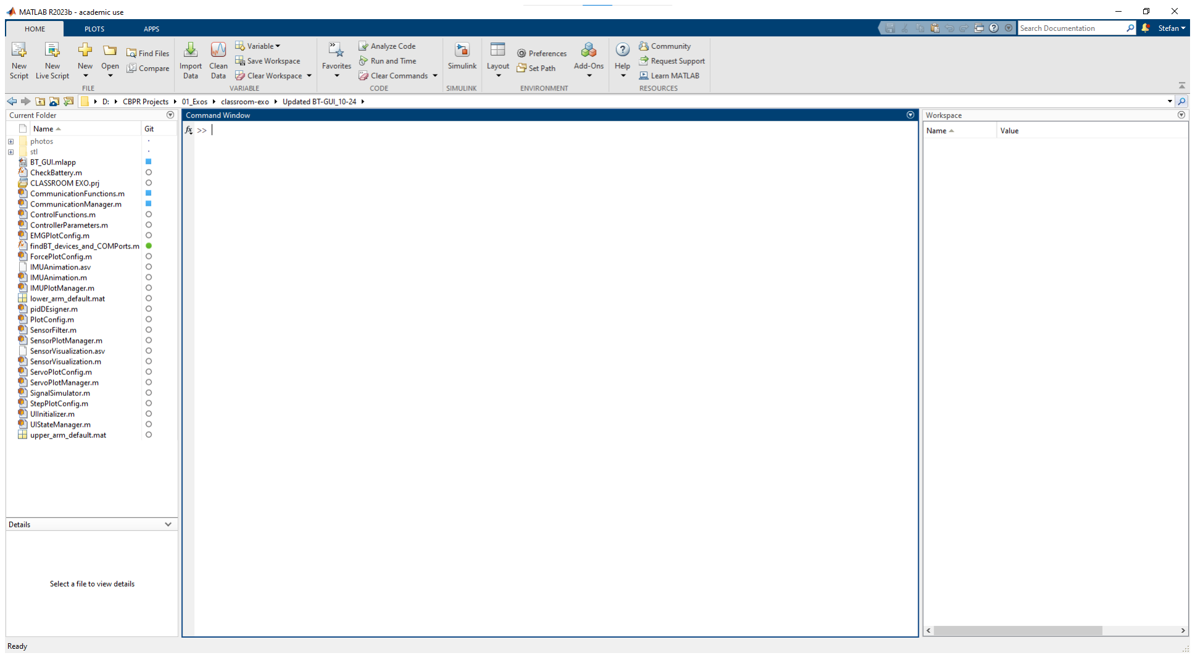
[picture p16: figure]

Figure 6.2: Glimpse of the MATLAB IDE by Mathworks.

6.2. EMBEDDED SOFTWARE | 3

## 6.2 Embedded Software

Summary

In this section we will walk you through the functionalities in the embedded code that is running directly on the SAMD21 chip of the Arduino Nano 33 IoT. With the embedded code, we enable Bluetooth Classic communication, different control algorithms for the motor, IMU integration as well as battery and device status indications. This makes the Classroom Exo more User friendly, while also offering a compatible GUI in MATLAB to easily change between control modes.

### 6.2.1 Setting up Bluetooth Classic Communication

The Arduino Nano 33 IoT has two separate chips on its board. The SAMD21 ist the heart of the microcontroller, which is running the main program that handles serial communication, reading the sensors and controlling the servo motor. The second chip, the WiFi NINA 102 module, enables us to use WiFi, Bluetooth BLE or Bluetooth Classic to communicate with the world outside of the microcontroller. The WiFi Nina chip essentially repeats, what the bigger SAMD21 chip sent to it, and passes it through to the outside. This signal can then be received by our MATLAB GUI.

The Classroom Exo should already have Bluetooth enabled, there are two ways to test if the Bluetooth Setup was already completed:

| Check available Bluetooth devices on your mobile phone
| Check available Bluetooth devices in the Bluetooth settings on Windows

If the device shows up on both connection managers, your Classroom Exo is ready to go. If the device does not show up, check that the Battery is charged and refer to our more comprehensive Guide on how to setup the Bluetooth Communication.

### 6.2.2 Control Algorithms in the embedded Software

Our embedded software enables you to run the Classroom Exo with different control modes, using the signals from the angle, force and sEMG sensor.

Embedded PID Controller

| standard P-I- or D controller using Kp, Ki and Kd,
| standard P-I- or D controller using design and control parameters,

Thresholding Control using Force Sensor The Force Sensor, which is located at the wrist cuff, enables us to implement

| a simple threshold based control,
| an admittance/proportional control

Thresholding Control using sEMG Sensor

| a simple threshold based control with either one sEMG sensor,
| or a simple threshold based control with two sEMG sensors

More information on how the Algorithms work, can be found in the more comprehensive Guide!

## 6.3 GUI in MATLAB

Summary

This section shows the MATLAB Front-End, which consists of an intuitive Graphical User Interface (GUI). The GUI communicates via Bluetooth Classic with te embedded code on the Arduino. The GUI enables controlling the Classroom Exo with a simulated P-/I-/D-Controller, Thresholding based on the Force or sEMG sensor. The wireless communication enables updating setting, streaming adds safety and freedom to move in space The fast communication also enables a simulatneus 3D animation of the Classroom Exo based on realtime IMU and angle data in the user interface. Additional information, like control mode and battery percentage, are also shown to the user.

### 6.3.1 Getting your MATLAB ready

Before we can use the GUI, you will need to install MATLAB and some additional Packages. Using the Addon Manager you can install the following packages, if you didn’t already do that during your initial MATLAB installation. The following packages are essential for using the complete GUI:

| Control System Toolbox (version 23.2)
| Instrument Control Toolbox (version 23.2)
| Robotics System Toolbox (version 23.2)
| Sensor Fusion and Tracking Toolbox (version 23.2)
| Signal Processing Toolbox (version 23.2)
| Symbolic Math Toolbox (version 23.2)

Hint

The MATLAB GUI was developed in Version R2023b, and tested for both R2023b and R2024a, so we CAN NOT guarantee that all the functionalities of the GUI will work with either older or newer versions!

6.3. GUI IN MATLAB | 5

### 6.3.2 Pairing your Classroom Exo with Windows 10 onward

Hint

Pairing the Bluetooth device was tested on Windows 10 and 11. So we cannot guarantee that it works with other operating systems! As of right now there is no support for MacOSx or Linux, and they are NOT planned for future releases!

To use the device, you must pair it with your Laptop/PC:

1. Power the BT device on
2. In Windows go to System Settings → Bluetooth and other devices → Add devices → Bluetooth
3. Now search for new available devices and pair the desired device e.g. xx CLASSROOM EDU EXO PRO.

After pairing the device, you can use it with the MATLAB GUI.

### 6.3.3 Getting started with the GUI

Open the MATLAB application by double-clicking on the file. Now, the MATLAB app will search for available Bluetooth devices, as you can see in Figure 6.3, that match our device naming structure.

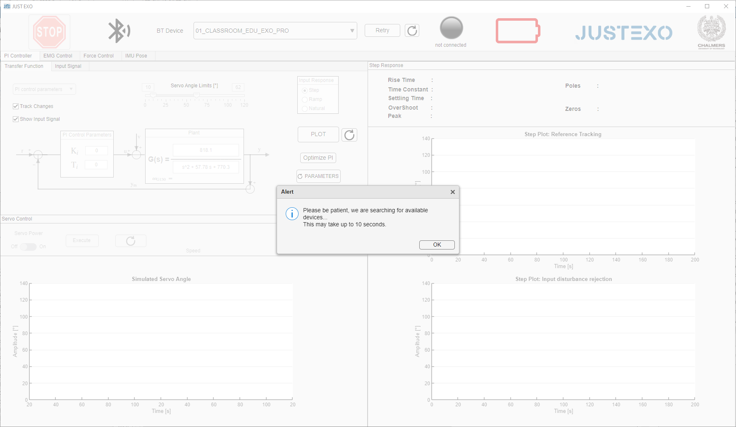
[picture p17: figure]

Figure 6.3: Startup page of the MATLAB GUI searching for available Bluetooth devices.

From the drop-down menu you are now able to select your desired device, and just hit the connect button. When the connection was successful, you will be able to see the updated Bluetooth symbol, the status led and battery icon.

Now, you can select the tab with the control mode that you want to try out.

PID Control Tab

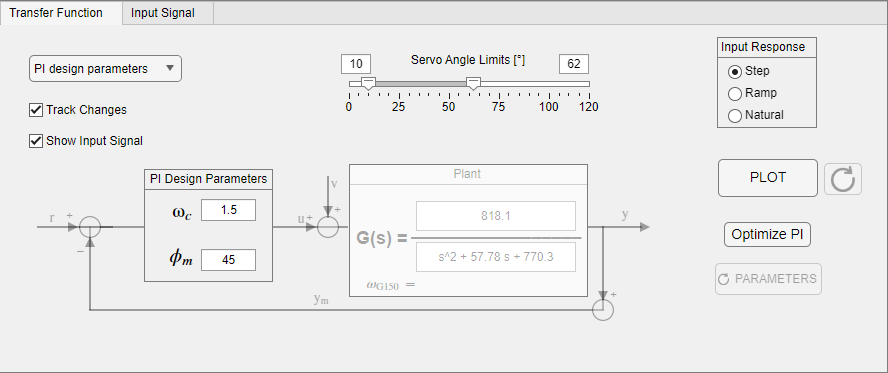
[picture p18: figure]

Figure 6.4: The controller can be designed by different parameters, such as the design parameters ωc and ϕm.

With the initial values you will have a system response that exceeds safe limits. Now, you should adjust the values so you get the desired control system behaviour.

To speed things up a bit, we’ve implemented an optimization algorithm in the Optimize PI button. As you can see in Figure 6.5 the PI-controller responds a lot slower, and does not exceed the desired limits of the the step input signal.

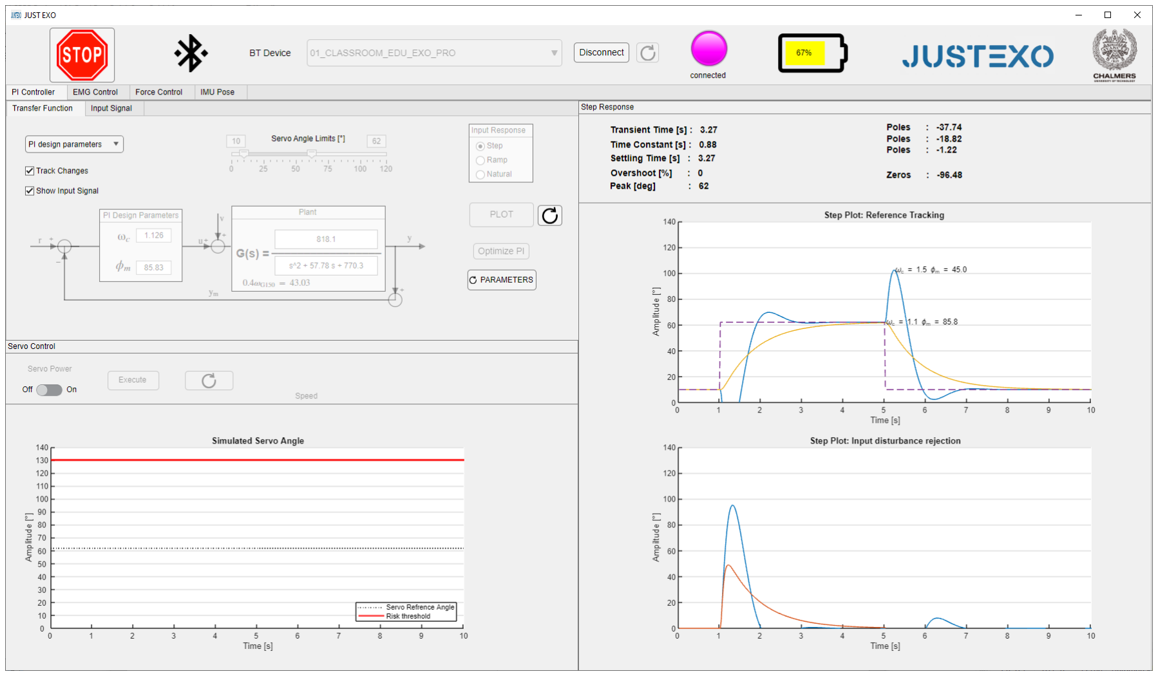
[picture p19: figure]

Figure 6.5: The controller can be optimized by an automatic algorithm.

6.3. GUI IN MATLAB | 7

Force Control Tab

If you want to use the threshold-based force control, go to the Force Control Tab. There a predefined settings for the thresholds and servo motor speed. You can just hit the Start button, and try out how the resistance feels against your wrist. You can see Force Control Tab interface in Figure 6.6.

You can adjust the force thresholds really easily: change the value on the threshold sliders and hit Apply Thresholds - this will restart the plot from zero with the newly selected threshold values.

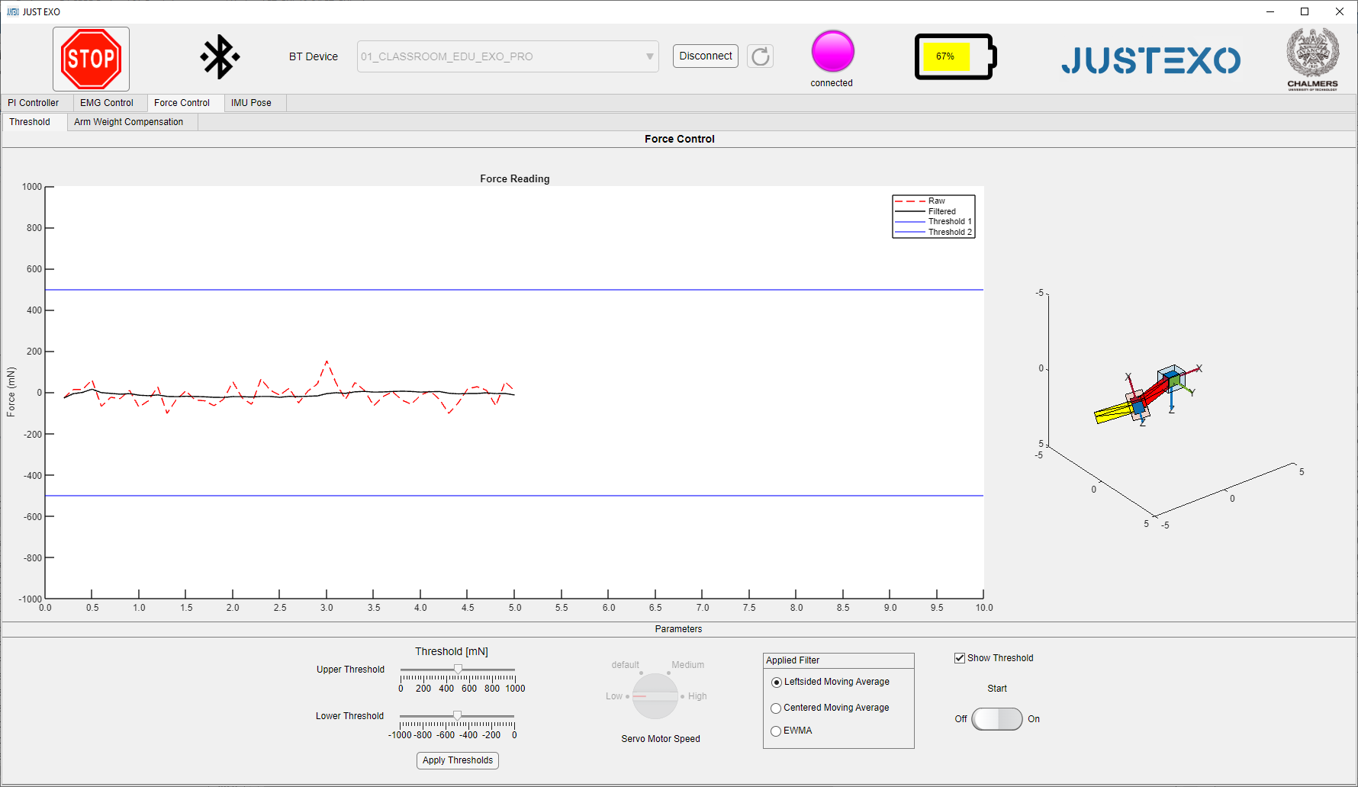
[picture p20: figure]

Figure 6.6: The Force Control Tab interface enables you to control the servo motor by applying pressure to the wrist cuff on the Exoskeleton.

You can also observe how different filters act on the signal quality. The filters on the radio-buttons are just for display purposes, and have no effect on the motor control itself.

On the right hand side, you can see a 3D-plot that displays a reference of the Exoskeleton based on IMU and angle sensor data. When you turn, or move the upper arm of you Exo, you can observe the movement in the liveplot. When the servomotor moves, you can see how the lower arm moves in reference to the upper arm.

sEMG Control Tab

If you now want to use the sEMG based control, go to the EMG Control Tab. You will find predefined settings for the thresholds and servo motor speed, as well as the sEMG channel. You can see EMG Control Tab interface in Figure 6.7.

Now, connect your sEMG sensor to a big muscle (i.e. biceps brachii) and plug the cable into the AUX port with the label EMG 0. If you want to use the other channel, you also have to change the channel in the drop-down menu!

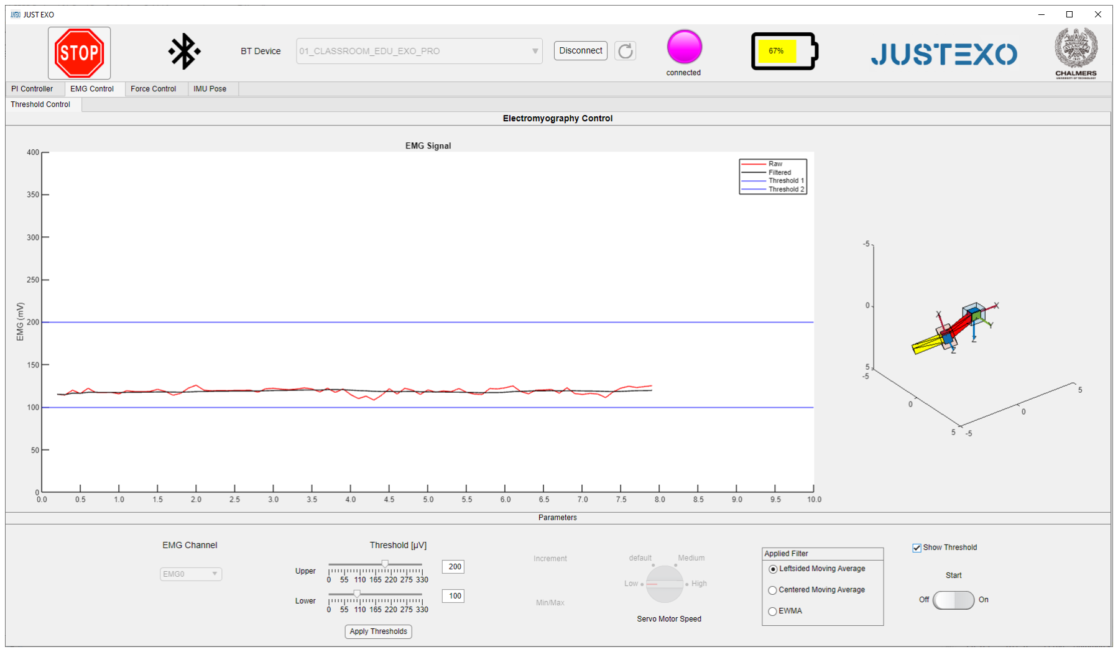
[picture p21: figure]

Figure 6.7: The sEMG Control Tab interface enables you to control the servo motor by flexing and relaxing your muscles.

Again, you can hit the Start button and try to control the servo motor with your muscle activation.

On the right hand side, you will find the same 3D liveplot as in the Force Control Tab.

6.3. GUI IN MATLAB | 9

### 6.3.4 Disconnecting from your device

Before powering off your Exoskeleton it is crucial to disconnect your Matlab GUI properly! Just hit the disconnect button, this will reset the Exoskeletton to it’s initial mode - so you will see the led button blinking blue again. Your Matlab interface will reset, and start searching for paired devices again.

If you want to exit your GUI, you can now just close the Matlab application; and also turn off the Exoskeletton manually.

### 6.3.5 Emergency Stop

If you do not feel comfortable using the Exoskeleton anymore, or a dangerous situation occurs there are two options of shutting down the servo motor movements.

1. Hitting the Emergency Stop button in the GUI - this turns off the motor power supply and disconnects the device from your MATLAB GUI. You will need to close the GUI before you can use it again.
2. Hitting the led power button on your Exoskeleton manually - this powers off the entire Exoskeleton without properly disconnecting from your MATLAB GUI. You will need to remove your paired device from the Windows settings, and start from the very beginning of this tutorial!

# Acronyms

GUI | Graphical User Interface. 1, 3, 4, 5
IDE | Integrated Development Environment. 1, 2
sEMG | Surface Electromyography. 1, 3, 4

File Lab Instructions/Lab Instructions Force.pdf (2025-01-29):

# Laboration: Force control of The Classroom Exo

DD.MM.YYY

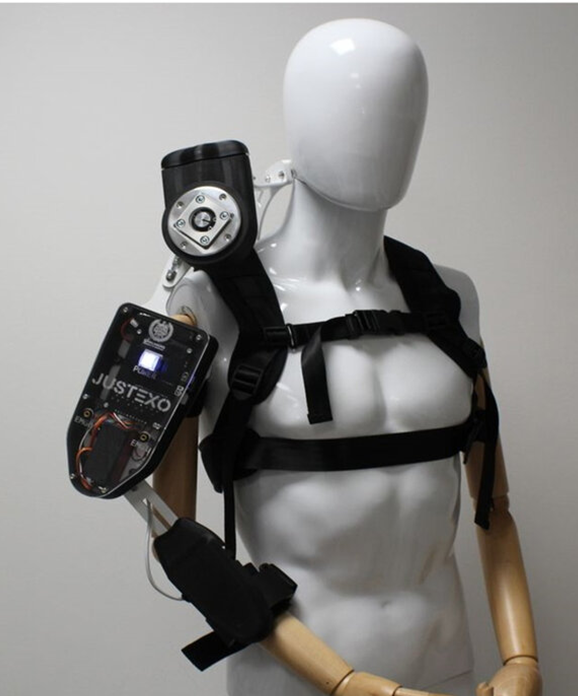
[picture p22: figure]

CONTENTS | i

## Contents

1 Lab Introduction | 1
1.1 Risk section | | 1
1.2 Learning objectives | | 1
1.3 Prerequisite knowledge | | 2
1.4 Materials and methods | | 2
1.5 To do at home before the lab | | 2
2 Introduction to the Exoskeleton | 3
2.1 Setting up the Classroom Exo | | 3
2.1.1 | Adjusting the exoskeleton | | 4
2.1.2 | Connecting to the device and starting the GUI | | 6
3 Force controller | 8
3.1 Introduction | | 8
3.2 Force controller setup | | 8
3.3 Exercises | | 10
3.3.1 | Default sensitivity | | 10
3.3.2 | Rehabilitation scenario | | 10
3.3.3 | Worker scenario | | 11
3.3.4 | Servo speed | | 11
3.4 Discussion | | 12
4 Typical errors and Troubleshooting | 12

1 LAB INTRODUCTION | 1

## 1 Lab Introduction

Summary

In this chapter you will find the necessary documentation to setup your Classroom Exo, and try out the Force options. We have prepared some Lab exercises, to help you learn more about the force control options!

An exoskeleton is a wearable mechanical structure that enhances or restores the physical abilities of the wearer by providing external support or amplification of movements [6]. As the field of robotics grows leaps and bounds with every passing day as the world of STEM aims to integrate technology with humans to aid and support or enhance activities of daily living. Education leveraging these technologies has however been lacking. This lab is intended for use at a university level and is a derivative of a project aimed at converting an open-source exoskeleton into educational material [6]. The Classroom Exo, the product that we will be using through the course of this lab, is a student-friendly optimized version of the EduExo Pro - An Advanced Robotic Exoskeleton Kit developed by Auxivo AG.

### 1.1 Risk section

The Classroom Exo is not categorized as a medical device. Instead, its primary focus is educational. It is designed to provide hands-on experience with various control systems. There are some risks associated with the use of the Classroom Exo. Listed below are the potential risks, what has been done to prevent them, and the possible causes of these risks.

| Muscle fatigue: Muscle fatigue can occur during prolonged use, as the Classroom Exo is some- what heavy. To minimize this risk, an ergonomic design and proper usage guidelines have been implemented.
| Injury risk: The risk of injury is very low, but it still exists. The primary cause is misalignment between the Classroom Exo’s mechanical joints and the user’s shoulder and elbow joints. This risk has been minimized through proper calibration, an emergency stop feature, and clear instructions for how to put on the Classroom Exo.

### 1.2 Learning objectives

The goal of this lab is to provide hands-on experience with the Classroom Exo as a practical example of applying engineering principles within the biomedical field. Throughout the lab, you will explore how force sensors can be used to control an exoskeleton. By experimenting with different thresholding levels you will consider the practical applications of force-controlled exoskeletons, understanding how and why they are used in different scenarios. By the end of this lab you should be able to:

| Implement force control on an exoskeleton and adjust threshold settings.
| Explain how threshold settings influence exoskeleton movement, and analyze its impact on perfor- mance and safety.

1 LAB INTRODUCTION | 2
| Evaluate the practical applications for this control method in terms of use case and user safety.

### 1.3 Prerequisite knowledge

There is no specific prerequisite knowledge required for this lab. Any student group interested in product design, user safety, or gaining insight into biomedical engineering principles can benefit from this lab. However, due to the complexity of the system, the use of MATLAB, and potential troubleshooting, this lab may be most suitable for engineering students.

### 1.4 Materials and methods

For this lab, you will need a Bluetooth-enabled computer and MATLAB 2023b (although newer versions should also work). We will be interfacing with the exoskeletons using the “Updated BT-GUI” MATLAB application. Additionally, you will need one exoskeleton and a 2.5 and 3,0 Allen Key to adjust the arm length of the exoskeleton to fit the anatomy of the student who will be wearing the exoskeleton.

### 1.5 To do at home before the lab

To make the most of the limited time you will have with the exoskeletons, you must come to the lab session well-prepared. Unforeseen issues or complications with the setup of the exoskeletons may arise, so proper preparation will ensure you have as much hands-on time as possible with the exoskeleton. Therefore before the lab asks you to:

1. Download MATLAB 2023b.
2. Download the “Updated BT-GUI 10-24” folder from the GitHub link: https://github.com/fabianjust/classroom-exo (https://github.com/fabianjust/classroom-exo)
3. Download and install the following MATLAB packages:
| Control System Toolbox (version 23.2)
| Instrument Control Toolbox (version 23.2)
| Robotics System Toolbox (version 23.2)
| Sensor Fusion and Tracking Toolbox (version 23.2)
| Signal Processing Toolbox (version 23.2)
| Symbolic Math Toolbox (version 23.2)
4. Read the lab PM thoroughly.

2 INTRODUCTION TO THE EXOSKELETON | 3

## 2 Introduction to the Exoskeleton

Exoskeletons are increasingly being incorporated into rehabilitative settings, such as walking assists for people who have undergone spinal cord injuries, strokes, etc., in physiotherapy, and occupational therapy [4]. Although aimed to be used in educational settings only, the Classroom Exo is an exoskeleton connected to the upper part of the body, over the shoulder, and the upper and lower arm, with a spring support to help lift the arm Figure 1. Programmed on Arduino, it has three control systems -proportional–integral—derivative controller (PID Controller), Electromyography signals from the muscles, and a force sensor on the wrist, the software of which is accessible as open-source, with a classroomfriendly graphical interface implemented on MATLAB.

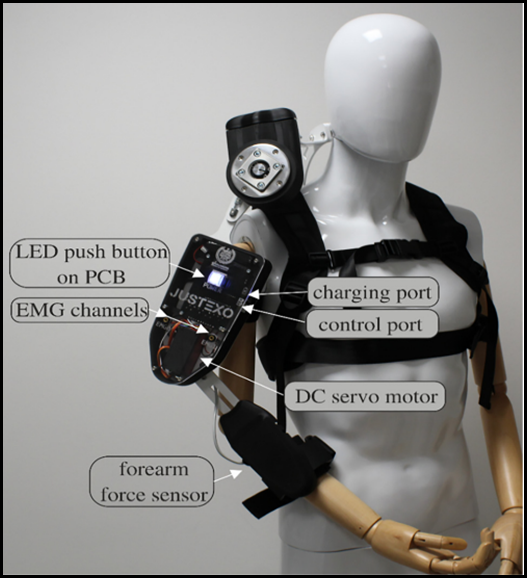
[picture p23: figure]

Figure 1: The Classroom Exo and its adaptations from EduExo Pro

### 2.1 Setting up the Classroom Exo

While putting on the exoskeleton it is helpful if one person holds it up and another tightens the straps.

1. Put on the vest and fasten the buckles.
2. Make sure that the shoulder part of the exoskeleton is aligned with your shoulder, which can be seen in Figure 2. And then tighten the chest and waist straps.

2 INTRODUCTION TO THE EXOSKELETON | 4

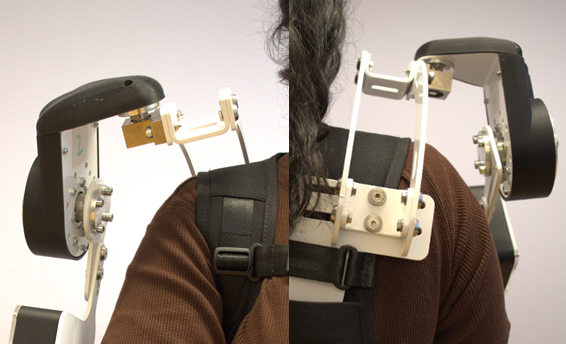
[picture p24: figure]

Figure 2: Shoulder joint aligned (left) and misaligned (right).

3. Tighten the straps around the elbow and the wrist and check alignment with the elbow joint according to Figure 3.

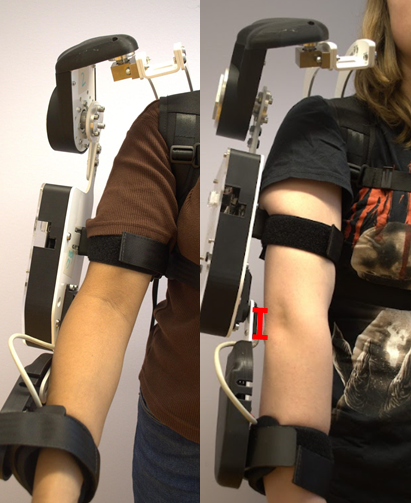
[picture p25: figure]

Figure 3: Correct alignment of elbow joint (left) and incorrect alignment (right), misalignment marked in red.

4. If the Classroom Exo has the correct joint alignment as seen in figure 4 and 3, proceed to section
2.1.2. If not, proceed with section 2.1.1 “Adjusting the exoskeleton”.

### 2.1.1 Adjusting the exoskeleton

To be able to adjust the arm length of the Classroom Exo, a 2.5 and 3.0 Allen Key is needed.

1. Under the shoulder joint on the back of the exoskeleton you can find two bolts for which the 3.0 Allen Key fits, the bolts are marked in Figure 4. Loosen these, align shoulder joints according to Figure 2 and tighten the bolts.

2 INTRODUCTION TO THE EXOSKELETON | 5

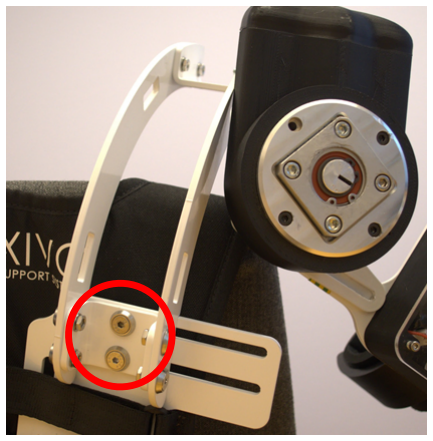
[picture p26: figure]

Figure 4: Bolts for adjusting shoulder breadth in red.

2. To align the elbow, loosen the bolts on the inside of the shoulder joint illustrated in Figure 5. Use the 3.0 Allen key to do this. Slide the arm such that the elbow joint of the exoskeleton and the user is aligned such as in Figure 3. Tighten the bolts.

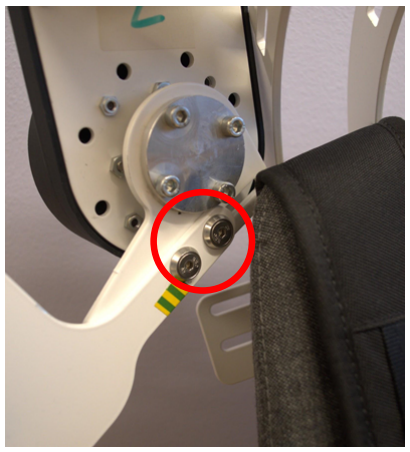
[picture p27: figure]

Figure 5: Bolts to adjust upper arm length for elbow alignment marked in red.

3. To adjust the position of the wrist cuff, loosen the bolt on the lower part on the arm of the exoskeleton marked in Figure 6, using the 2.5 Allen key. Adjust length and tighten the bolts.

2 INTRODUCTION TO THE EXOSKELETON | 6

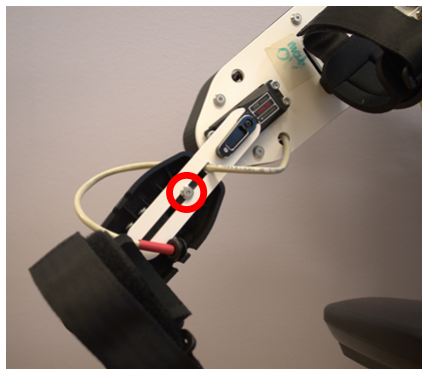
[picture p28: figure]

Figure 6: Bolts to adjust lower arm length for positioning of wrist cuff marked in red.

### 2.1.2 Connecting to the device and starting the GUI

1. Turn on the exoskeleton by pushing the “LED push button on PCB” as seen in Figure 7. It should blink blue indicating that it is searching for a Bluetooth device.
2. When you are connecting to the exoskeleton for the first time, go to your computer’s Bluetooth settings and add a Bluetooth device. When pairing, the name of your device will be XX CLASSROOM EDU EXO PRO where the XX is a number between 01 to 08 depending on which exoskeleton you have.

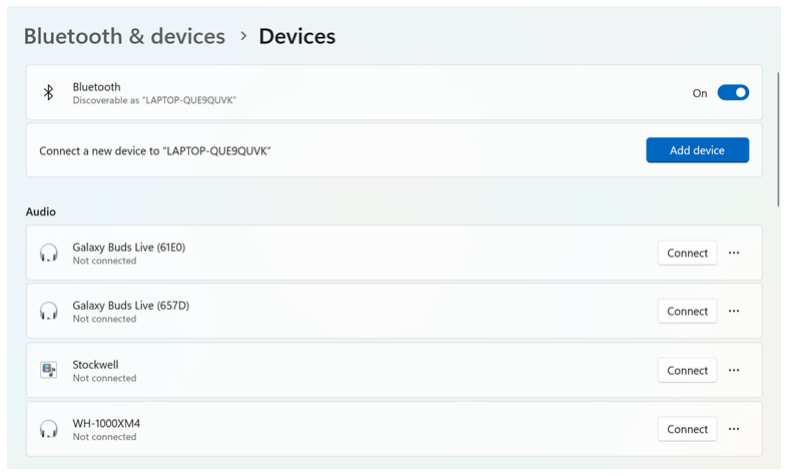
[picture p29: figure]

Figure 7: Pairing to a Bluetooth device for the first time.

3. In your computer’s display settings set the screen size to 100%.

2 INTRODUCTION TO THE EXOSKELETON | 7

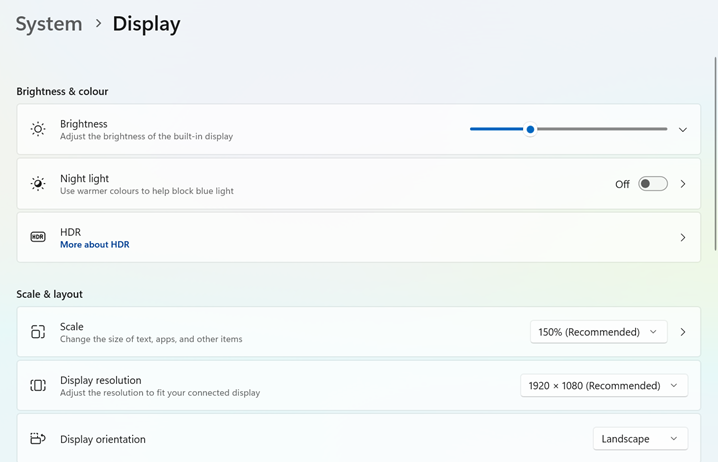
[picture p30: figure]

Figure 8: Changing screen sizing.

4. Open MATLAB, locate the BT GUI file and double click on it. Or locate the file in your file explorer and select open with MATLAB. If you open the file in MATLAB’s app designer, click run.
5. When the GUI is opened, choose the correct Bluetooth device, and click connect.

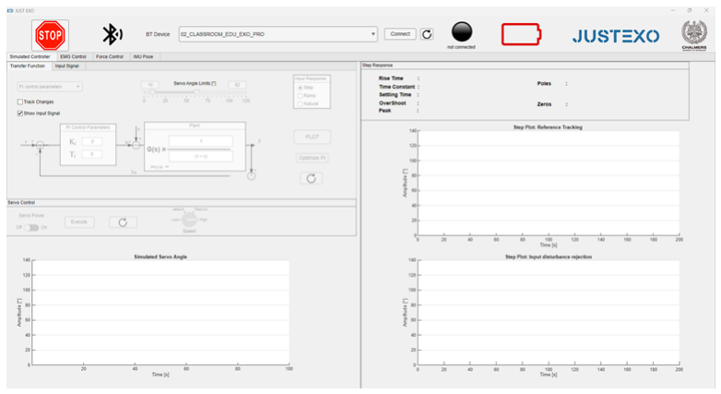
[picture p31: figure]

Figure 9: Connecting to the Bluetooth device.

The power button on the exoskeleton and the indicator in the GUI should change color to either green, yellow or red depending on the battery level.

3 FORCE CONTROLLER | 8

## 3 Force controller

### 3.1 Introduction

Force control enables systems to detect and respond to external forces, making them adaptable to environmental changes or user force input [2]. This concept is widely used across engineering, from rehabilitation to industrial applications [5]. In rehabilitation, exoskeletons use force control to either assist in or add resistance to patients’ intended motions [2]. By using exoskeletons we can allow for movements that the patient otherwise could not perform, avoid over-extension, relieve physiotherapists’ work burden, and gradually reduce the assistance as the patient regains strength [2, 1].

Additionally, it might be useful in industrial settings for workers where the motor in the exoskeleton helps them in movements when the sensors detect forces or strains that would otherwise be harmful to the worker’s body, thus preventing injuries [3].

The Classroom Exo uses strain gauges at the wrist cuff to detect forces, see Figure 1. When these sensors experience deformation due to a force, they change their resistance, altering the voltage over them [6]. These sensors allow the exoskeleton to detect a voltage difference when an upward force exceeds a threshold and subsequently flex the elbow joint. Similarly, exceeding a downward threshold causes the elbow joint to extend, moving the arm to a straighter position.

### 3.2 Force controller setup

The exoskeleton should be put on before starting this part.

1. Choose the “Force control” tab, and then the “Threshold” tab, which can be seen in Figure 10.

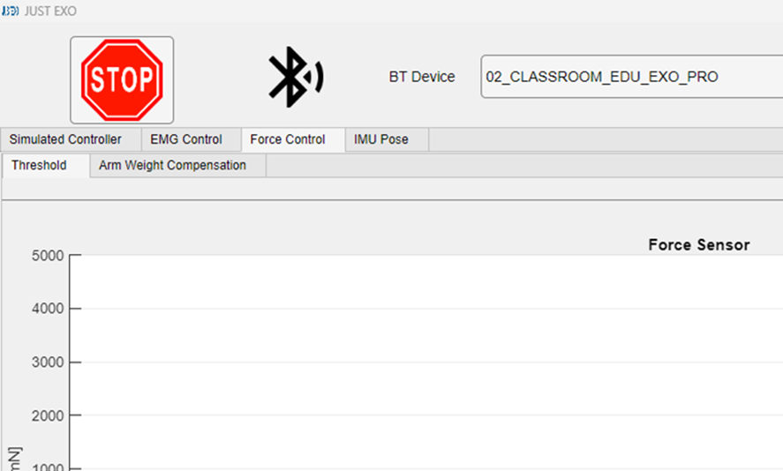
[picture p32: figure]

Figure 10: Choosing the force control tab (red) and the threshold tab (blue).

2. At the bottom of the tab, you can see the force control parameters. Where you can change the upper and lower threshold force limits, the servo motor speed, and the applied filter. See Figure 11.

3 FORCE CONTROLLER | 9

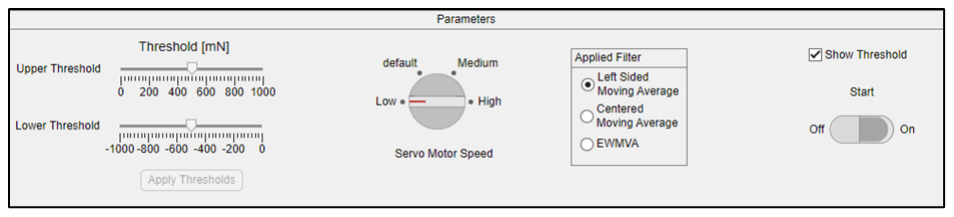
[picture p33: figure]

Figure 11: The tunable force control parameters.

3. Ensure the “show threshold” box which you can see in Figure 11 is checked to see when the force on the wrist cuff exceeds the upper or lower threshold. 4. Click start. When trying out the force control by flexing and extending your arm you should see something like this:

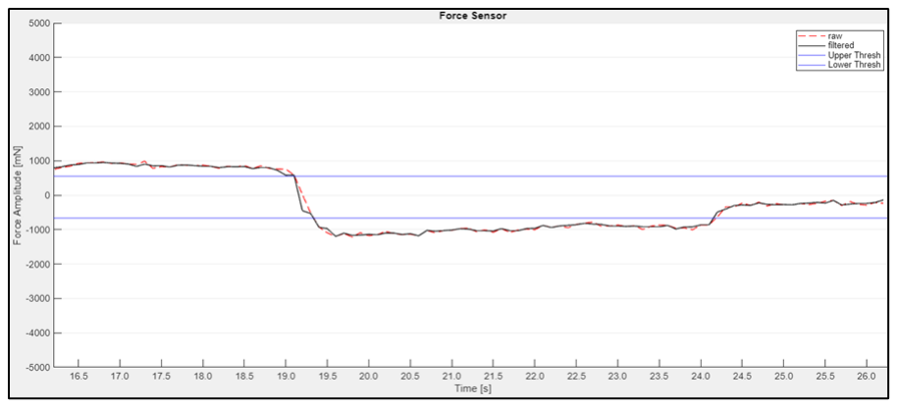
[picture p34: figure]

Figure 12: Force sensor data.

5. When changing the threshold values, make sure to click “apply thresholds” and turn the start button off and then on again.

3 FORCE CONTROLLER | 10

### 3.3 Exercises

Attention

OBS! You can break pieces of the exoskeleton. Don’t try to exceed thresholds by more than necessary.

This section outlines a series of exercises to be completed during the allotted lab time. These exercises are designed to deepen your understanding of how Force control can be applied in combination with the Classroom Exo. The results of the exercises must be documented in a separate report. The question exercises are meant to be discussed within a group.

### 3.3.1 Default sensitivity

Test the default threshold settings (lower threshold = -500 mN, upper threshold = 500 mN) to understand what force control feels like.

Tasks:

1. Flex your bicep to exceed the higher threshold and see how the elbow joint flexes.
2. Try to straighten your arm, exerting force in the other direction exceeding the lower threshold causing the joint to straighten.

Question:

1. Is there a maximum and minimum angle of the elbow flexion and how does this play into user safety?

### 3.3.2 Rehabilitation scenario

To simulate a rehabilitation scenario we will now increase the sensitivity of the system.

Tasks:

1. Set the lower threshold value to -100, and set the upper threshold to 100.
2. Now try to flex your arm and extend it. How is it different from the default threshold settings?

Questions:

1. In what real-life use-cases for exoskeletons would there be for high-sensitivity sensing of forces?
2. Experiment with different thresholds. Can you find a usable threshold for the use case you thought of? If you couldn’t find a usable threshold, why?

3 FORCE CONTROLLER | 11
3. In a rehabilitation setting, how can lower versus higher sensitivity affect the users in terms of support and safety?
4. Are there any other safety risks in this use case?

### 3.3.3 Worker scenario

In this section, we will simulate an industrial worker as a user by setting the thresholds so we have a low-sensitivity system.

Tasks:

1. Try setting the lower threshold to a higher setting and the upper threshold to a lower value. A suggestion would be to set the lower threshold to a value close to -1000, and the upper threshold to 1000.
2. Test it out, what does it feel like?

Questions:

1. In what real-life use cases for exoskeletons would there be for low-sensitivity sensing of forces?
2. Experiment with different thresholds, which ones do you think work best for this scenario and why? If you couldn’t find a usable threshold, why?
3. How does a lower versus higher sensitivity affect the users in this use case in terms of support and safety in this use case?
4. Are there any other safety risks in this use case?

### 3.3.4 Servo speed

We will now experiment with servo speed and reflect on the uses.

Tasks:

1. Set the speed to low, medium, and then high.
2. Test it out, what does it feel like?

Questions:

1. What would be the benefit or drawback of having a static servo speed?
2. What would be the benefit or drawback of having a dynamic servo speed?
3. Reflect on this in terms of use case and safety.

4 TYPICAL ERRORS AND TROUBLESHOOTING | 12

### 3.4 Discussion

For the best learning experience, feel free to discuss the results your group obtained from each step between groups to gain understanding and new perspectives.

1. What differed between your answers and the answers of other groups?
2. Why did your answers or conclusions differ?
3. Did your discussions between groups lead to new insights or ideas? If so, what were they?

## 4 Typical errors and Troubleshooting

In this section, we present typical errors and issues encountered during testing of the Classroom Exo.

1. If you experience that the exoskeleton arm switches between extending and contracting, almost vibrating, it might be because the upper and lower thresholds are too close to each other.
2. If the thresholds are not showing or the signal is not showing after changing the thresholds, then click “apply thresholds” and turn the start button off and then on again. Wait for the signal to appear.

Hint

You can find a more comprehensive Troubleshooting documentation in the Manual on our GitHub!

REFERENCES | 13

## References

[1] Thomas Dickmann et al. “An Adaptive Mechatronic Exoskeleton for Force-Controlled Finger Rehabilitation”. In: Frontiers in Robotics and AI 8 (Sept. 2021). issn: 2296-9144. doi: 10.3389/frobt. 2021.716451. (https://doi.org/10.3389/frobt.2021.716451)
[2] Piotr Falkowski and Kajetan Jeznach. “Simulation of a control method for active kinesiotherapy with an upper extremity rehabilitation exoskeleton without force sensor”. In: Journal of NeuroEngineering and Rehabilitation 21.1 (Feb. 2024). issn: 1743-0003. doi: 10.1186/s12984-024-01316-x. (https://doi.org/10.1186/s12984-024-01316-x)
[3] Ali Golabchi, Andrew Chao, and Mahdi Tavakoli. “A Systematic Review of Industrial Exoskeletons for Injury Prevention: Efficacy Evaluation Metrics, Target Tasks, and Supported Body Postures”. In: Sensors 22.7 (Apr. 2022), p. 2714. issn: 1424-8220. doi: 10.3390/s22072714. (https://doi.org/10.3390/s22072714)
[4] Deborah Hill et al. “WHAT ARE USER PERSPECTIVES OF EXOSKELETON TECHNOLOGY? A LITERATURE REVIEW”. In: International Journal of Technology Assessment in Health Care 33.2 (2017), pp. 160–167. issn: 1471-6348. doi: 10.1017/s0266462317000460. (https://doi.org/10.1017/s0266462317000460)
[5] Lin Lang et al. “Scale Force Control of an Exoskeleton for Human Performance Augmentation”. In: Journal of Intelligent amp; Robotic Systems 106.1 (Sept. 2022). issn: 1573-0409. doi: 10.1007/ s10846-022-01611-6. (https://doi.org/10.1007/s10846-022-01611-6)
[6] Mohammed Al-Tashi et al. “Classroom-ready open-source educational exoskeleton for biomedical and control engineering”. In: at - Automatisierungstechnik 72.5 (May 2024), pp. 460–475. issn: 2196-677X. doi: 10.1515/auto-2023-0208. (https://doi.org/10.1515/auto-2023-0208)

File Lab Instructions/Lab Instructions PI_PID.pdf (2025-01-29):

# Laboration: PI/PID control of The Classroom Exo

DD.MM.YYY


CONTENTS | i

## Contents

1 Lab Introduction | 1
1.1 Risk section | | 1
1.2 Learning objectives | | 1
1.3 Prerequisite knowledge | | 2
1.4 Materials and methods | | 2
1.5 To do at home before the lab | | 2
2 Introduction to the Exoskeleton | 3
2.1 Setting up the Classroom Exo | | 3
2.1.1 | Adjusting the exoskeleton | | 4
2.1.2 | Connecting to the device and starting the GUI | | 6
3 PI/PID controller | 8
3.1 PI/PID setup | | 9
4 Exercises | | 13
4.1 Tasks and questions PI | | 13
4.1.1 | Trying out the PI controller | | 13
4.1.2 | Changing the input response | | 14
4.1.3 | Working with the PI controller | | 15
4.2 Tasks and questions PID | | 17
4.2.1 | Trying out the PID controller | | 17
4.2.2 | Changing the input response | | 18
5 Discussion | | 19
6 Typical errors and Troubleshooting | 19

1 LAB INTRODUCTION | 1

## 1 Lab Introduction

Summary

In this chapter you will find the necessary documentation to setup your Classroom Exo, and try out the PI and PID controller options. We have prepared some Lab exercises, to help you learn more about control theory.

An exoskeleton is a wearable mechanical structure that enhances or restores the physical abilities of the wearer by providing external support or amplification of movements [3]. As the field of robotics grows leaps and bounds with every passing day as the world of STEM aims to integrate technology with humans to aid and support or enhance activities of daily living. Education leveraging these technologies has however been lacking. This lab is intended for use at a university level and is a derivative of a project aimed at converting an open-source exoskeleton into educational material [3]. The Classroom Exo, the product that we will be using through the course of this lab, is a student-friendly optimized version of the EduExo Pro - An Advanced Robotic Exoskeleton Kit developed by Auxivo AG.

### 1.1 Risk section

The Classroom Exo is not categorized as a medical device. Instead, its primary focus is educational. It is designed to provide hands-on experience with various control systems. There are some risks associated with the use of the Classroom Exo. Listed below are the potential risks, what has been done to prevent them, and the possible causes of these risks.

Muscle fatigue: Muscle fatigue can occur during prolonged use, as the Classroom Exo is somewhat heavy. To minimize this risk, an ergonomic design and proper usage guidelines have been implemented.

Injury risk: The risk of injury is very low, but it still exists. The primary cause is misalignment between the Classroom Exo’s mechanical joints and the user’s shoulder and elbow joints. This risk has been minimized through proper calibration, an emergency stop feature, and clear instructions for how to put on the Classroom Exo.

### 1.2 Learning objectives

The goal of this section is to explore various step signals, plant designs, and control parameter settings to observe their effect on overshoot, oscillations, and residual error on step responses. You will reflect on the importance of control system design in biomedical applications where precise control is important for user safety.

Identify a PID controller’s components and explain their effect on a system’s behavior.

Demonstrate tuning of PID control and design parameters, predict and analyze their impact on system performance such as overshoot, oscillation and error.

1 LAB INTRODUCTION | 2

Evaluate the importance of the PI/PID controller in biomedical applications, specifically as applied to exoskeletons.

### 1.3 Prerequisite knowledge

For this section of the lab the students are expected to have a basic understanding of control systems, specifically P, PI and PID-controllers, the impact of each component in a PID controller and knowledge of the design and control parameters stated in the book “Fundamentals of Control Technology” [2] . The students should be familiar with concepts like overshoot, oscillations and steady-state error. For example would this lab fit well in an engineering programme in the first control system course after introducing PID controllers.

### 1.4 Materials and methods

For this lab, you will need a Bluetooth-enabled computer and MATLAB 2023b (although newer versions should also work). We will be interfacing with the exoskeletons using the “Updated BT-GUI” MATLAB application. Additionally, you will need one exoskeleton and a screwdriver to adjust the arm length of the exoskeleton to fit the anatomy of the student who will be wearing the exoskeleton.

### 1.5 To do at home before the lab

To make the most of the limited time you will have with the exoskeletons, you must come to the lab session well-prepared. Unforeseen issues or complications with the setup of the exoskeletons may arise, so proper preparation will ensure you have as much hands-on time as possible with the exoskeleton. Therefore before the lab asks you to:

1. Download MATLAB 2023b.
2. Download the “Updated BT-GUI 10-24” folder from the GitHub link: https://github.com/fabianjust/classroom-exo (https://github.com/fabianjust/classroom-exo)
3. Download and install the following MATLAB packages:

Control System Toolbox (version 23.2)

Instrument Control Toolbox (version 23.2)

Robotics System Toolbox (version 23.2)

Sensor Fusion and Tracking Toolbox (version 23.2)

Signal Processing Toolbox (version 23.2)

Symbolic Math Toolbox (version 23.2)

4. Read the lab PM thoroughly.

2 INTRODUCTION TO THE EXOSKELETON | 3

## 2 Introduction to the Exoskeleton

Exoskeletons are increasingly being incorporated into rehabilitative settings, such as walking assists for people who have undergone spinal cord injuries, strokes, etc., in physiotherapy, and occupational therapy [1]. Although aimed to be used in educational settings only, the Classroom Exo is an exoskeleton connected to the upper part of the body, over the shoulder, and the upper and lower arm, with a spring support to help lift the arm Figure 1. Programmed on Arduino, it has three control systems -proportional–integral—derivative controller (PID Controller), Electromyography signals from the muscles, and a force sensor on the wrist, the software of which is accessible as open-source, with a classroomfriendly graphical interface implemented on MATLAB.


Figure 1: The Classroom Exo and its adaptations from EduExo Pro

### 2.1 Setting up the Classroom Exo

While putting on the exoskeleton it is helpful if one person holds it up and another tightens the straps.

1. Put on the vest and fasten the buckles.
2. Make sure that the shoulder part of the exoskeleton is aligned with your shoulder, which can be seen in Figure 2. And then tighten the chest and waist straps.

2 INTRODUCTION TO THE EXOSKELETON | 4


Figure 2: Shoulder joint aligned (left) and misaligned (right).

3. Tighten the straps around the elbow and the wrist and check alignment with the elbow joint according to Figure 3.


Figure 3: Correct alignment of elbow joint (left) and incorrect alignment (right), misalignment marked in red.

4. If the Classroom Exo has the correct joint alignment as seen in figure 4 and 3, proceed to section
2.1.2. If not, proceed with section 2.1.1 “Adjusting the exoskeleton”.

### 2.1.1 Adjusting the exoskeleton

To be able to adjust the arm length of the Classroom Exo, a 2.5 and 3.0 Allen Key is needed.

1. Under the shoulder joint on the back of the exoskeleton you can find two bolts for which the 3.0 Allen Key fits, the bolts are marked in Figure 4. Loosen these, align shoulder joints according to Figure 2 and tighten the bolts.

2 INTRODUCTION TO THE EXOSKELETON | 5


Figure 4: Bolts for adjusting shoulder breadth in red.

2. To align the elbow, loosen the bolts on the inside of the shoulder joint illustrated in Figure 5. Use the 3.0 Allen key to do this. Slide the arm such that the elbow joint of the exoskeleton and the user is aligned such as in Figure 3. Tighten the bolts.


Figure 5: Bolts to adjust upper arm length for elbow alignment marked in red.

3. To adjust the position of the wrist cuff, loosen the bolt on the lower part on the arm of the exoskeleton marked in Figure 6, using the 2.5 Allen key. Adjust length and tighten the bolts.

2 INTRODUCTION TO THE EXOSKELETON | 6


Figure 6: Bolts to adjust lower arm length for positioning of wrist cuff marked in red.

### 2.1.2 Connecting to the device and starting the GUI

1. Turn on the exoskeleton by pushing the “LED push button on PCB” as seen in Figure 7. It should blink blue indicating that it is searching for a Bluetooth device.
2. When you are connecting to the exoskeleton for the first time, go to your computer’s Bluetooth settings and add a Bluetooth device. When pairing, the name of your device will be XX CLASSROOM EDU EXO PRO where the XX is a number between 01 to 08 depending on which exoskeleton you have.


Figure 7: Pairing to a Bluetooth device for the first time.

3. In your computer’s display settings set the screen size to 100%.

2 INTRODUCTION TO THE EXOSKELETON | 7


Figure 8: Changing screen sizing.

4. Open MATLAB, locate the BT GUI file and double click on it. Or locate the file in your file explorer and select open with MATLAB. If you open the file in MATLAB’s app designer, click run.
5. When the GUI is opened, choose the correct Bluetooth device, and click connect.


Figure 9: Connecting to the Bluetooth device.

The power button on the exoskeleton and the indicator in the GUI should change color to either green, yellow or red depending on the battery level.

3 PI/PID CONTROLLER | 8

## 3 PI/PID controller

Introduction The Classroom Exos’ software is capable of simulating two types of control systems: a PI controller and a PID controller. In total, six controllers are pre-installed. The first four are based on Bengt Lennartson’s theories from his book “Fundamentals of Control Technology”[2], while the remaining two are standard PI/PID controllers.

The PI controller consists of a proportional P action and an integrating I action. The PID controller also has a derivative D action. The design parameters that can be changed in the simulation for the PI controller are the upper crossover frequency (ωc) and the phase margin (ϕm, in Bengt’s book designated as ϕm). For the PID controller, a constant (β) can also be changed. The control parameters that can be changed for the PI controller are the integral gain (Ki) and the integral time constant (Ti). The control parameters that can be changed for the PID controller are the integral gain (Ki), the integral time constant (τ ), a constant (β), and the damping (ζ).

Once the parameters are set in the GUI and the system is operational, the arm will move according to the specified parameter values. There is a button that allows you to adjust the speed at which the Classroom Exo moves the arm. The standard servo motor speed is “default”, but there are also options for low, medium, and high speeds, see Figure 10.

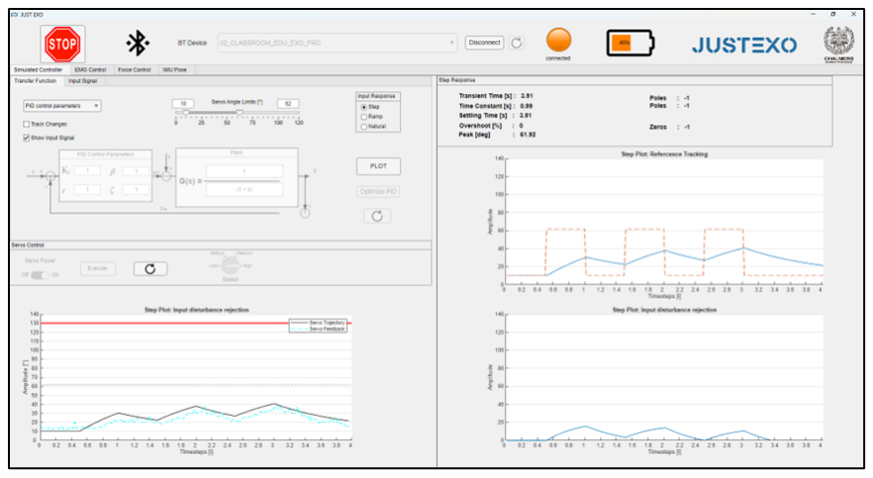
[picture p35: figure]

Figure 10: The GUI for the simulated PID control parameters.

There are three real-time measurement graphs available for monitoring system behavior. One graph tracks reference signals following (input (red) and output (blue)). The other two graphs are used to monitor input disturbance rejection. The graph in the right corner, shows the system’s response to a disturbance signal. It measures how well the system can reject or minimize the effect of disturbances that deviate the system from its desired state. The other graph next to it, has a clear red line at the top of the graph. This line is the danger zone, and it is important that the signal does not pass this line. The graph also shows the servo trajectory (the calculated trajectory) in black, and the servo feedback (how the motor actually moves) in blue.

3 PI/PID CONTROLLER | 9

### 3.1 PI/PID setup

The exoskeleton should be put on before starting this part. 1. Choose the “Simulated controller” tab, and then the “transfer function” tab, which can be seen in Figure 11.

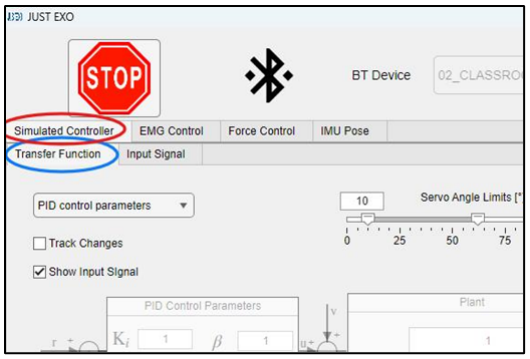
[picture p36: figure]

Figure 11: Choosing the simulated controller tab (red) and the transfer function tab (blue).

2. Choose input response, see Figure 12.

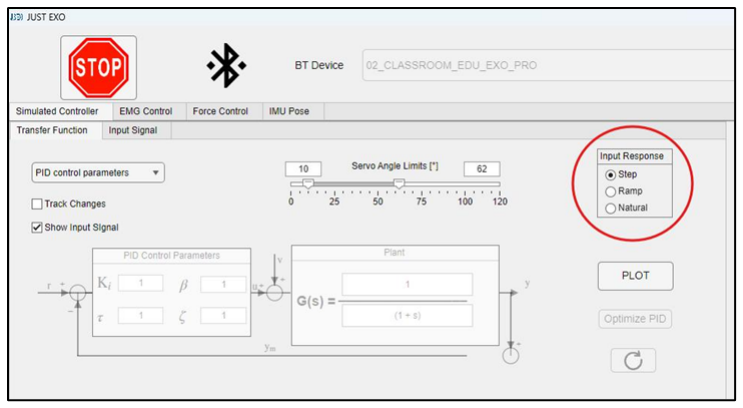
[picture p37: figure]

Figure 12: Choosing the input response.

3. In the dropdown menu, choose which controller you want to work with. See Figure 13.

3 PI/PID CONTROLLER | 10

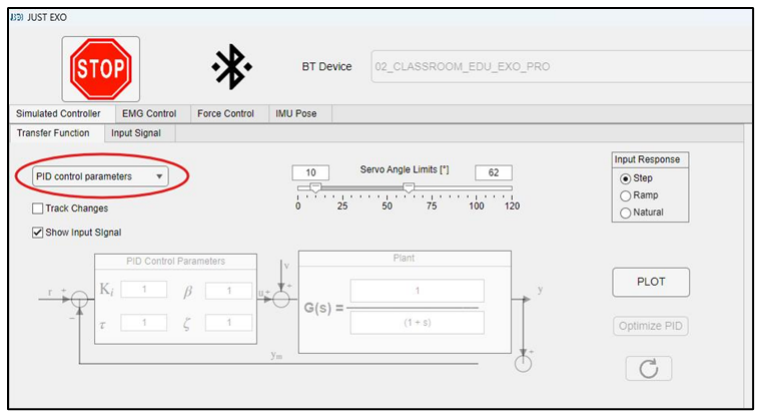
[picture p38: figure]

Figure 13: In the dropdown menu (red) choose controller.

4. Choose parameters, see Figure 14.

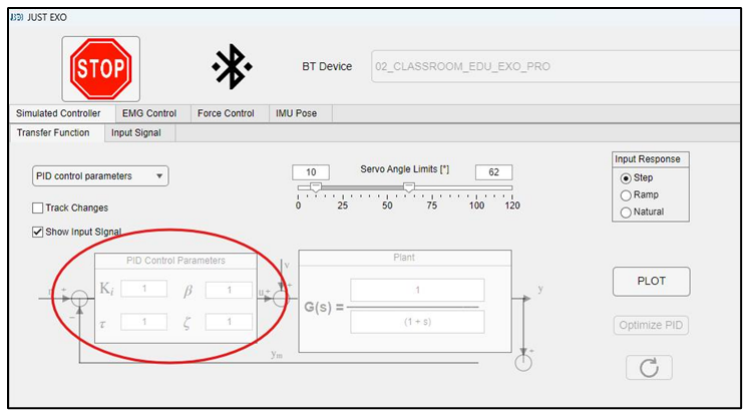
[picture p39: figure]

Figure 14: Change the different parameters.

5. Click on the input signal tab, see Figure 15.

3 PI/PID CONTROLLER | 11

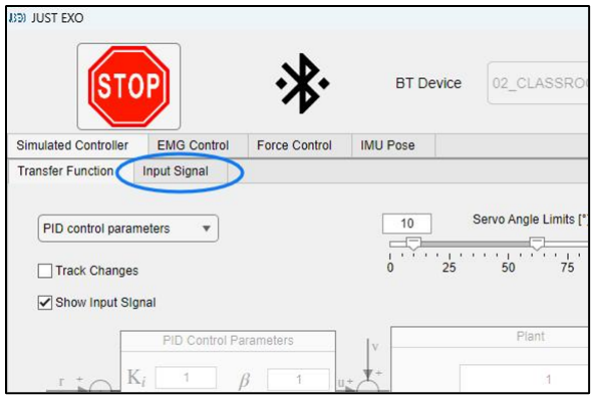
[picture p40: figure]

Figure 15: The input signal tab (blue).

6. In this tab, you can modify the parameters for the input signal, such as the period and the number of repetitions, to suit your needs. See Figure 16.

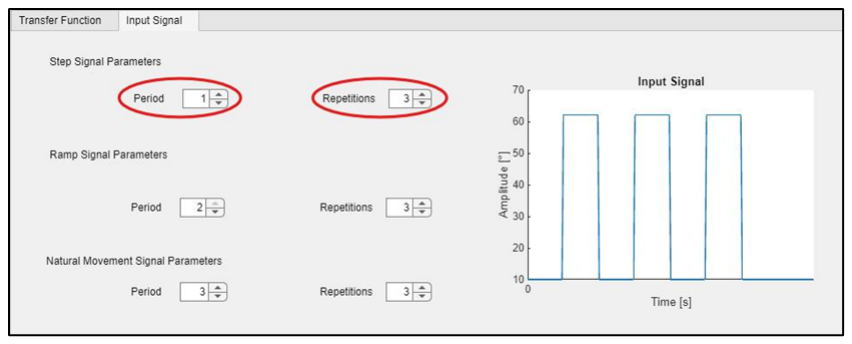
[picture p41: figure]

Figure 16: Choosing the period and repetitions

7. When you have chosen the parameters for the input response, go back to the “Transfer Function” tab, and click on plot. You should now see three different plots. See Figure 17 a. If you get an error that says “The used system (TF) is crosses the Danger zone (0°).”, see page 18 for more information.

3 PI/PID CONTROLLER | 12

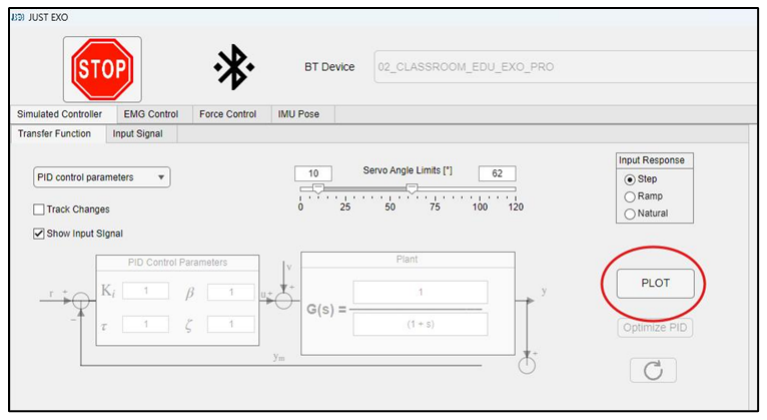
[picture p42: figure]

Figure 17: Click plot.

8. Below the title Servo Control, click on server power (on), see figure 19. The Classroom Exo should move to the reference angle.
9. Before clicking execute, you can change the speed. Click the knob-like button, and choose low, default, medium or high. See Figure 18. 10. Then click execute, see Figure 18. The Classroom Exo should then start moving. (The button should turn magenta/purple/pink) 11. If you click on the reset button next to the execute one, see Figure 18, the Classroom Exo should return to the reference angle and you should be able to click execute again.

Figure 18: Layout for servo control.

4 EXERCISES | 13

## 4 Exercises

This section outlines a series of exercises to be completed during the allotted lab time. These exercises are designed to deepen your understanding of how a simulated PI/PID control can be applied in combination with the Classroom Exo. The question exercises are meant to be discussed within a group.

### 4.1 Tasks and questions PI

Below are a number of tasks and questions related to the PI controller. These tasks are designed to help you explore the behavior of the PI controller under different conditions and parameter settings.

### 4.1.1 Trying out the PI controller

These initial tasks will allow you to get comfortable with the simulation interface and begin exploring how altering different parameters influences the system’s performance.

Task:

1. Choose the PI design parameters in the drop-down menu.
2. Set ωc = 2 and ϕm = 45
3. The click plot.
4. When the graphs have appeared, turn on the servo power and then click execute.
(a) If you can’t click on execute, then restart the GUI, see more information on page 18.

Questions :

1. What happens?
2. Why does it lead to this result?

Task:

1. Choose the PI control parameters in the drop-down menu.
2. Set Ki = 1.5 and Ti = 5.
3. The click plot.
4. When the graphs have appeared, turn on the servo power and then click execute.

Questions:

1. What happens?
2. Why does it lead to this result?

4 EXERCISES | 14

### 4.1.2 Changing the input response

Choose another input response, and go to the Input Signal tab. Now, change the parameter values for Period and Repetition to observe how the input signal affects the system. You may choose any period and repetition, however the period needs to be an integer value. This task is designed to help you understand the impact of the input signal on the system’s response.

Task:

1. Choose the PI design parameter
2. Set ωc = 2 and ϕm = 45
3. The click plot
4. When the graphs have appeared, turn on the servo power and then click execute.

Questions:

1. Is there any difference between this result, and the result from section 4.1.1?
(a) Why is there a difference?
2. How does the input response affect the control system?
3. Do you notice any difference in system response between step, ramp and natural input signal?

4 EXERCISES | 15

### 4.1.3 Working with the PI controller

Below are a series of general questions related to the PI controller. These questions involve parameter adjustments of the upper crossover frequency and phase margin, and exploring optimized values. To solve these tasks, begin by selecting parameter values for Period and Repetition in the input signal tab.

Task:

1. Choose the PI design parameter in the drop-down menu.
2. Increase crossover frequency ωc while the phase margin ϕm remains the same. What do you observe?
3. While still having a high crossover frequency ωc increase the phase margin ϕm. What do you observe?
4. Test other lower values for ωc and ϕm.

Questions:

1. How do the different parameter values affect the system’s behavior?
2. These parameters are dependent on each other and affect the system’s response. How does one choice affect the choice of another?
3. What happens with the system response if you keep one of the parameters constant, and change only the other?
4. How does the crossover frequency ωc affect stability at low phase margins?

Task:

1. Choose the PI control parameter in the drop-down menu.
2. Set the integral component Ki close to zero (e.g. 0.2).

Questions:

1. Can you see a steady state error?
2. How does a low Ki affect the steady-state error and the system’s stability?
3. What happens if you set Ki to a high value? Why?

Task:

1. Choose the PI control parameter in the drop-down menu.
2. Try out some different values of Ki and Ti.

4 EXERCISES | 16

Questions:

1. How does Ti affect the control system? Keep Ki constant.
(a) What would happen if Ti had a low value?
(b) What would happen if Ti had a high value?
2. How does Ki affect the control system? Keep Ti constant.
(a) What would happen if Ki had a low value?
(b) What would happen if Ki had a high value?

4 EXERCISES | 17

### 4.2 Tasks and questions PID

Below are several tasks and questions related to the PID controller. These tasks are designed to help you explore the behavior of the PID controller under different conditions and parameter settings

### 4.2.1 Trying out the PID controller

These initial tasks will allow you to get comfortable with the simulation interface and begin exploring how altering different parameters influences the system’s performance.

Task:

1. Choose the PID design parameters in the drop-down menu.
2. Set ωc = 3 , β = 5 and ϕm = 65.What happens?
3. Increase and decrease the crossover frequency ωc
4. Increase and decrease the phase margin ϕm

Questions:

1. How do the crossover frequency and phase margin affect the system’s behavior?
2. How do these parameters affect each other?
3. What happens if you keep one of the parameters constant and change only the other one?
4. How does the crossover frequency ωc affect stability at low phase margins?

Task:

1. Set β to 1.
2. Then set β to 30.

Questions:

1. What happens if you set β to 1?
2. What happens if β is larger?
3. What effect does the constant have on the controller?

Task:

1. Choose the PID control parameters in the drop-down menu.
2. Chose values for Ki, τ , and β. For example, set Ki = 1, τ = 10 and β = 12.
3. Try different values for the damping factor ζ.

4 EXERCISES | 18

Questions:

1. What happens to the system’s behavior when the damping factor ζ increases?
2. What effect does the damping factor ζ have on the system?
3. How do the Ki, β, τ , and ζ affect the control system’s performance?

Task:

1. Now hold β and ζ constant and set Ki close to zero.
2. Experiment with different values for τ

Questions:

1. What happens if you set Ki to a high value?
2. What effect does the integral component have on the system?
3. How do these two parameters affect the time it takes for the system to reach a steady state?
4. What effect does τ have on the system?
(a) What would happen if τ was large?

### 4.2.2 Changing the input response

Choose another input response, and go to the Input Signal tab. Now, change the parameter values for Period and Repetition to observe how the input signal affects the system. This task is designed to help you understand the impact of the input signal on the system’s response.

Task:

1. Choose the PID design parameter.
2. Set ωc = 3 , β = 5 and ϕm = 65.
3. Then click plot.
4. When the graphs have appeared, turn on the servo power and then click execute.

Questions:

1. Is there any difference between this result, and the result from section 4.2.1? Why or why not?
2. How does the input response affect the control system?
3. How does the system handle a step, ramp, and natural input?

5 DISCUSSION | 19

## 5 Discussion

For the best learning experience, feel free to discuss the results your group obtained from each step between groups to gain understanding and new perspectives.

1. What do the graphs tell you about the system’s behavior?
(a) What conclusions can you draw regarding parameter choices from these graphs? What can be deduced?
2. Compare the different controllers to each other. Which one works best for the Classroom Exo?
(a) Are there cases where the PI controller would work better than the PID, and vice versa?
3. How do PI and PID controllers influence user safety when applied in biomedical devices like exoskeletons? Consider factors such as system stability, responsiveness, and the potential for overshooting or oscillations.
(a) How could improper calibration or tuning of these controllers lead to risks for the user, such as joint misalignment or muscle strain?
(b) What are some preventative measures that could be taken to minimize these risks when implementing control systems in devices that support or augment human movement?

## 6 Typical errors and Troubleshooting

In this section, we present typical errors and issues encountered during testing of the Classroom Exo.

1. If you get an error message that says “The used system (TF) is crosses the Danger zone (0°). Please try another system or change the minimum servo angle limits.”, then you can increase the input server angle limit or change control parameters and plot again.
2. If you get this error message it is because you can’t choose a period that is not a whole number.
3. For design parameters, after plotting you cannot change the parameter values, this is a bug. Switch to another control in the drop-down menu. And switch back to the design parameter of your choice and you should be able to choose parameter values.
4. If you can’t click on execute after you clicked plot (the execute button is not visible), then you need to restart the GUI and connect to the Classroom Exo again.

Hint

You can find a more comprehensive Troubleshooting documentation in the Manual on our GitHub!

REFERENCES | 20

## References

[1] Deborah Hill et al. “WHAT ARE USER PERSPECTIVES OF EXOSKELETON TECHNOLOGY? A LITERATURE REVIEW”. In: International Journal of Technology Assessment in Health Care 33.2 (2017), pp. 160–167. issn: 1471-6348. doi: 10.1017/s0266462317000460. (https://doi.org/10.1017/s0266462317000460)
[2] Bengt Lennartson. Reglerteknikens grunder. sv. Studentliteratur AB, 2002. url: https : / / www . studentlitteratur.se/kurslitteratur/teknik/reglerteknik/reglerteknikens-grunder/ (visited on 01/27/2025).
[3] Mohammed Al-Tashi et al. “Classroom-ready open-source educational exoskeleton for biomedical and control engineering”. In: at - Automatisierungstechnik 72.5 (May 2024), pp. 460–475. issn: 2196-677X. doi: 10.1515/auto-2023-0208. (https://doi.org/10.1515/auto-2023-0208)

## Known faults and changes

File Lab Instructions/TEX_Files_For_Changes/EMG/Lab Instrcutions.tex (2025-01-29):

\documentclass[]{article}

%=========================
%      Includes
%=========================
\input{etc/packages}
\input{etc/abbreviations}
\input{etc/listingsstyle} % colorful listings (source code)
\input{etc/stlye}
\input{etc/arduinoLanguage}

\usepackage[backend=biber]{biblatex}
\addbibresource{etc/literature.bib}

\title{Laboration: EMG-control of The Classroom Exo}

\titlepic{}

\author{Linn Hellberg, Sushanthika Gnanasekaran, and Amanda Hoveklint}
\date{DD.MM.YYY}

\globalcounter{figure}

\begin{document}
\pagenumbering{gobble}
\maketitle \newpage

\pagenumbering{roman}

\tableofcontents
\newpage

\setcounter{page}{1}
\pagenumbering{arabic}
\include{frontmatter/text}
\newpage
\input{frontmatter/abbreviations} 
\printbibliography
\end{document}

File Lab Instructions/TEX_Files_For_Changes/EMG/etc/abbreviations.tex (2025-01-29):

% =========================================================
% Define abbreviations
% =========================================================

\newacronym{sEMG}{sEMG}{Surface Electromyography}
\newacronym{GUI}{GUI}{Graphical User Interface}
\newacronym{ROM}{ROM}{Range Of Motion}
\newacronym{ADC}{ADC}{Analog Digital Converter}
\newacronym{MOSFET}{MOSFET}{Metal-Oxide-Semiconductor Field-Effect Transistor}
\newacronym{RGB}{RGB}{Red-Green-Blue}
\newacronym{IDE}{IDE}{Integrated Development Environment}
\newacronym{PCB}{PCB}{Printed Circuit Board}
\newacronym{IPA}{IPA}{Isopropyl Alcohol}
\newacronym{BOM}{BOM}{Bill of Materials}
\newacronym{HTML}{HTML}{Hypertext Markup Language}
\newacronym{SMD}{SMD}{Surface-Mounted Device}
\newacronym{SMT}{SMT}{Surface Mount Technology}
\newacronym{IC}{IC}{Integrated Circuit}
\newacronym{LED}{LED}{Light Emitting Diode}
\newacronym{USB}{USB}{Universal Serial Bus}
\newacronym{PPE}{PPE}{Personal Protective Equipment}
\newacronym{PWM}{PWM}{Pulse Width Modulation}
\newacronym{IMU}{IMU}{Inertial Measurement Unit}
\newacronym{PLA}{PLA}{Polylactic Acid}
\newacronym{ABS}{ABS}{Acrylonitrile Butadiene Styrene}
\newacronym{PETG}{PETG}{Polyethylene Terephthalate Glycol}
\newacronym{PID}{PID}{Proportional-Derivative-Integral}

%\newacronym{}{}{}

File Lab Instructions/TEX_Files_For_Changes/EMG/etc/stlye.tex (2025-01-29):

% =========================================================
% Define the main document style and font
%
% This syle mainly inherits from the templaye avalilable
% in Moddle, by DAndexer, SEntacher
%
% TODO: use fancyhdr
% =========================================================

\ifdefined\withTimesNewRoman
% Set font to Times New Roman. Note that fontspec requires lualatex or xelatex.
% Requires ttf-mscorefonts-installer on Debian.
\usepackage{fontspec}
\setmainfont{Times New Roman}
\fi

\usepackage{a4wide}

%Seitenraender/Zeilenabstand
\usepackage[a4paper,left=2.5cm,right=2.5cm,top=2.5cm,bottom=4cm]{geometry}
\usepackage{setspace}
\onehalfspacing
\setlength{\parindent}{0pt}
\setlength{\headheight}{18pt}
\setlength{\parskip}{5pt plus 2pt minus 1pt}
%\setcellgapes{3pt}

%Formatierung der Fussnote
%\usepackage[bottom,hang]{footmisc}

%Formatierung für Kopfzeile
\usepackage[headsepline,automark]{scrlayer-scrpage} 
\setlength{\headsep}{15mm}
\clearpairofpagestyles 
\ihead{\headmark}
\ohead{\pagemark}
\addtolength{\topmargin}{1\baselineskip}

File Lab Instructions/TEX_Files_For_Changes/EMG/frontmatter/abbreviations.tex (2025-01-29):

% =========================================================
% Define abbreviations in etc/abbreviations!
% =========================================================
\printnoidxglossaries

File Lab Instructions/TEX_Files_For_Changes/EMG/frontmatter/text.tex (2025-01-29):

% !TeX spellcheck = en_US
%\setcounter{chapter}{6} % set chapter counter so we begin at chapter 5
%\chapter{Laboration: PI/PID control of The Classroom Exo}

\section{Lab Introduction}

\begin{tcolorbox}[colback=blue!5!white,colframe=blue!75!black,title=Summary]
	In this chapter you will find the necessary documentation to setup your Classroom Exo, and try out the EMG options. We have prepared some Lab exercises, to help you learn more about surface Electromyography and control.
\end{tcolorbox}
\vspace{0.5cm}
 
An exoskeleton is a wearable mechanical structure that enhances or restores the physical abilities of the wearer by providing external support or amplification of movements \cite{AlTashi2024}. As the field of robotics grows leaps and bounds with every passing day as the world of STEM aims to integrate technology with humans to aid and support or enhance activities of daily living. Education leveraging these technologies has however been lacking. 
This lab is intended for use at a university level and is a derivative of a project aimed at converting an open-source exoskeleton into educational material \cite{AlTashi2024}. The Classroom Exo, the product that we will be using through the course of this lab, is a student-friendly optimized version of the EduExo Pro - An Advanced Robotic Exoskeleton Kit developed by Auxivo AG. 

\subsection{Risk section}
The Classroom Exo is not categorized as a medical device. Instead, its primary focus is educational. It is designed to provide hands-on experience with various control systems. There are some risks associated with the use of the Classroom Exo. Listed below are the potential risks, what has been done to prevent them, and the possible causes of these risks.
\begin{itemize}[]
	\item \textbf{Muscle fatigue:} Muscle fatigue can occur during prolonged use, as the Classroom Exo is somewhat heavy. To minimize this risk, an ergonomic design and proper usage guidelines have been implemented.
	\item \textbf{Skin irritation:} Some users have experienced skin irritation from reacting to surface electrodes. Although it is uncommon, skin-friendly materials are used to minimize this risk. Irritation typically occurs after prolonged contact with the EMG sensors.
	\item \textbf{Injury risk:} The risk of injury is very low, but it still exists. The primary cause is misalignment between the Classroom Exo's mechanical joints and the user's shoulder and elbow joints. This risk has been minimized through proper calibration, an emergency stop feature, and clear instructions for how to put on the Classroom Exo.
\end{itemize}
	
\subsection{Learning objectives}
The goal of this section is to explore how EMG signals are generated from muscle activity and can be used to control a system. You will be introduced to basic anatomy and physiology to assist with electrode placement and reflect on the challenges of using biological signals, including signal strength, interference, reference signals, signal propagation, and processing. 

\begin{itemize}[]
	\item Set up the EMG measurement system to control exoskeleton movement.
	\item Troubleshoot and resolve common EMG-related signal setup issues and evaluate how different factors affect the measured signal. 
	\item Reflect on applications of EMG-controlled systems in terms of use cases and patient safety. 
	
\end{itemize}
	
\subsection{Prerequisite knowledge}
The prerequisite knowledge for this section is basic engineering principles such as signal propagation, disturbance signals, and signal processing. Knowledge of basic muscle physiology yields an optimal experience in this lab. Our recommendation would be to introduce this section in the first year of a biomedical engineering programme; however, this could be introduced later or earlier (with some preparations from the teacher) and still be beneficial for the students.  

\subsection{Materials and methods}
For this lab, you will need a Bluetooth-enabled computer and MATLAB 2023b (although newer versions should also work). We will be interfacing with the exoskeletons using the “Updated BT-GUI” MATLAB application. Additionally, you will need one exoskeleton and a screwdriver to adjust the arm length of the exoskeleton to fit the anatomy of the student who will be wearing the exoskeleton. For the EMG control, you will need three electrodes and one/two Myoware sensors (depending on the number of channels used). 

\subsection{To do at home before the lab}
To make the most of the limited time you will have with the exoskeletons, you must come to the lab session well-prepared. Unforeseen issues or complications with the setup of the exoskeletons may arise, so proper preparation will ensure you have as much hands-on time as possible with the exoskeleton. Therefore before the lab asks you to:  
\begin{enumerate}[]
	\item Download MATLAB 2023b.
	\item Download the “Updated BT-GUI\_10-24”  folder from the GitHub link: \url{https://github.com/fabianjust/classroom-exo}
	\item Download and install the following MATLAB packages: 
	\begin{itemize}[]
		\item Control System Toolbox (version 23.2)
		\item Instrument Control Toolbox (version 23.2)
		\item Robotics System Toolbox (version 23.2)
		\item Sensor Fusion and Tracking Toolbox (version 23.2)
		\item Signal Processing Toolbox (version 23.2)
		\item Symbolic Math Toolbox (version 23.2)
	\end{itemize}
	\item Read the lab PM thoroughly.
\end{enumerate}

\newpage
	
\section{Introduction to the Exoskeleton}
Exoskeletons are increasingly being incorporated into rehabilitative settings, such as walking assists for people who have undergone spinal cord injuries, strokes, etc., in physiotherapy, and occupational therapy \cite{Hill2017}. Although aimed to be used in educational settings only, the Classroom Exo is an exoskeleton connected to the upper part of the body, over the shoulder, and the upper and lower arm, with a spring support to help lift the arm \autoref{fig:fig02}. Programmed on Arduino, it has three control systems - proportional–integral–-derivative controller (PID Controller), Electromyography signals from the muscles, and a force sensor on the wrist, the software of which is accessible as open-source, with a classroom-friendly graphical interface implemented on MATLAB. 

\begin{figure}[H]
	\centering
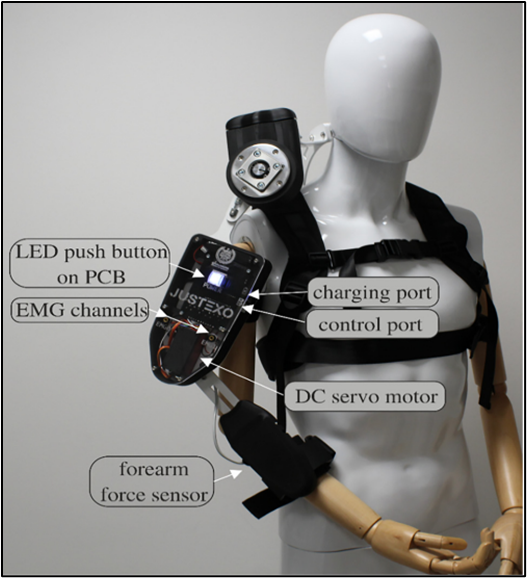
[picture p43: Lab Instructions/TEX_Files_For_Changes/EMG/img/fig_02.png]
	
	\caption{The Classroom Exo and its adaptations from EduExo Pro }
	\label{fig:fig02}
\end{figure}

\subsection{Setting up the Classroom Exo}
While putting on the exoskeleton it is helpful if one person holds it up and another tightens the straps.
\begin{enumerate}[]
	\item Put on the vest and fasten the buckles. 
	\item Make sure that the shoulder part of the exoskeleton is aligned with your shoulder, which can be seen in \autoref{fig:fig03}. And then tighten the chest and waist straps.
\end{enumerate}

\begin{figure}[H]
	\centering
	
	\caption{Shoulder joint aligned (left) and misaligned (right).}
	\label{fig:fig03}
\end{figure}

\begin{enumerate}[]
	\setcounter{enumi}{2}
	\item Tighten the straps around the elbow and the wrist and check alignment with the elbow joint according to \autoref{fig:fig04}. 
\end{enumerate}

\begin{figure}[H]
	\centering
	
	\caption{Correct alignment of elbow joint (left) and incorrect alignment (right), misalignment marked in red.}
	\label{fig:fig04}
\end{figure}

\begin{enumerate}[]
	\setcounter{enumi}{3}
	\item If the Classroom Exo has the correct joint alignment as seen in figure 4 and 3, proceed to section 2.1.2. If not, proceed with section 2.1.1 “Adjusting the exoskeleton”.
\end{enumerate}

\subsubsection{Adjusting the exoskeleton}
To be able to adjust the arm length of the Classroom Exo, a 2.5 and 3.0 Allen Key is needed.

\begin{enumerate}[]
	\item Under the shoulder joint on the back of the exoskeleton you can find two bolts for which the 3.0 Allen Key fits, the bolts are marked in \autoref{fig:fig05}. Loosen these, align shoulder joints according to \autoref{fig:fig03} and tighten the bolts. 
\end{enumerate}

\begin{figure}[H]
	\centering
	\begin{center}
		\begin{tikzpicture}
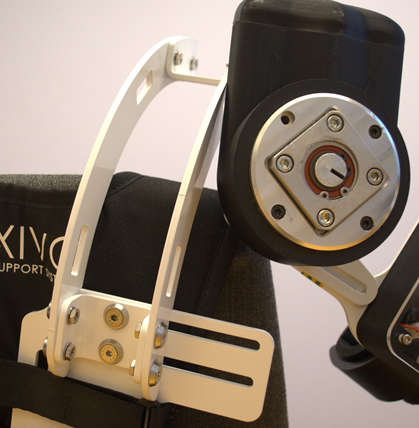
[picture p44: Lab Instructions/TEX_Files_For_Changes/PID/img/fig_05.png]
			\node(a){};
			\node at(a.center)[draw, red,line width=3pt,circle, minimum width=45pt, minimum height=45pt,rotate=-40,yshift=-65pt]{};
		\end{tikzpicture}   
	\end{center}
	\caption{Bolts for adjusting shoulder breadth in red.}
	\label{fig:fig05}
\end{figure}

\begin{enumerate}[]
	\setcounter{enumi}{1}
	\item To align the elbow, loosen the bolts on the inside of the shoulder joint illustrated in \autoref{fig:fig06}. Use the 3.0 Allen key to do this. Slide the arm such that the elbow joint of the exoskeleton and the user is aligned such as in \autoref{fig:fig04}. Tighten the bolts.
\end{enumerate}

\begin{figure}[H]
	\centering
	\begin{center}
		\begin{tikzpicture}
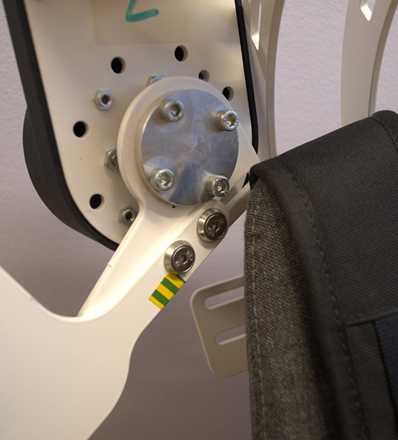
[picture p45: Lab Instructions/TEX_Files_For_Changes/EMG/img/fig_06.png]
			\node(a){};
			\node at(a.center)[draw, red,line width=3pt,circle, minimum width=45pt, minimum height=45pt,rotate=0,yshift=-7pt, xshift=-1pt]{};
		\end{tikzpicture}   
	\end{center}
	\caption{Bolts to adjust upper arm length for elbow alignment marked in red.}
	\label{fig:fig06}
\end{figure}

\begin{enumerate}[]
	\setcounter{enumi}{2}
	\item To adjust the position of the wrist cuff, loosen the bolt on the lower part on the arm of the exoskeleton marked in \autoref{fig:fig07}, using the 2.5 Allen key. Adjust length and tighten the bolts.
\end{enumerate} 

\begin{figure}[H]
	\centering
	\begin{center}
		\begin{tikzpicture}
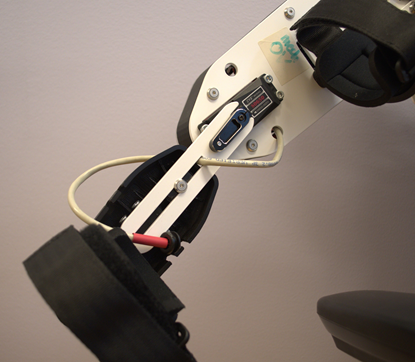
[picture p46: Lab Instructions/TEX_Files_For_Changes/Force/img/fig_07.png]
			\node(a){};
			\node at(a.center)[draw, red,line width=3pt,circle, minimum width=15pt, minimum height=15pt,rotate=0,xshift=-12pt, yshift=-2pt]{};
		\end{tikzpicture}   
	\end{center}
	\caption{Bolts to adjust lower arm length for positioning of wrist cuff marked in red.}
	\label{fig:fig07}
\end{figure}
\subsubsection{Connecting to the device and starting the GUI}
\begin{enumerate}[]
	\item Turn on the exoskeleton by pushing the “LED push button on PCB” as seen in \autoref{fig:fig08}. It  should blink blue indicating that it is searching for a Bluetooth device.
	\item When you are connecting to the exoskeleton for the first time, go to your computer's Bluetooth settings and add a Bluetooth device. When pairing, the name of your device will be XX\_CLASSROOM\_EDU\_EXO\_PRO where the XX is a number between 01 to 08 depending on which exoskeleton you have.
\end{enumerate}

\begin{figure}[H]
	\centering
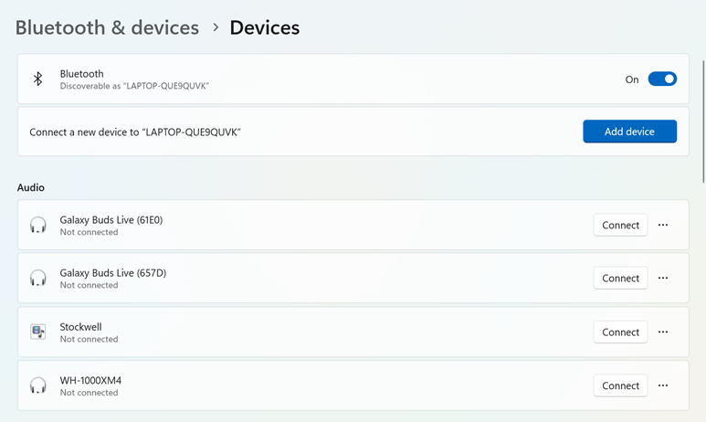
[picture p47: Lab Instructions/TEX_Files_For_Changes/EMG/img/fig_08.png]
	
	\caption{Pairing to a Bluetooth device for the first time.}
	\label{fig:fig08}
\end{figure}
\begin{enumerate}[]
	\setcounter{enumi}{2}
	\item In your computer's display settings set the screen size to 100\%.
\end{enumerate}
\begin{figure}[H]
	\centering
	
	\caption{Changing screen sizing.}
	\label{fig:fig09}
\end{figure}

\begin{enumerate}[]
	\setcounter{enumi}{3}
	\item Open MATLAB, locate the BT\_GUI file and double click on it. Or locate the file in your file explorer and select open with MATLAB. If you open the file in MATLAB’s app designer, click run.
	\item When the GUI is opened, choose the correct Bluetooth device, and click connect. 
\end{enumerate}

\begin{figure}[H]
	\centering
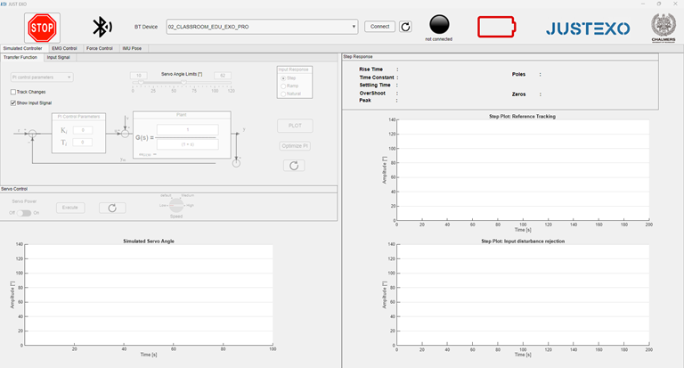
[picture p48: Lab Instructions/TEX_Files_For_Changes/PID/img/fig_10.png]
	
	\caption{Connecting to the Bluetooth device.}
	\label{fig:fig10}
\end{figure}

The power button on the exoskeleton and the indicator in the GUI should change color to either green, yellow or red depending on the battery level.

\newpage
\section{EMG controller}
\subsection{Introduction}
The technique to measure motor control - the electrical activity from the muscles in the human body is called Electromyography (EMG). Every time our muscles contract and expand, a difference in electrical potential can be observed, which can be measured using surface electrodes (surface or sEMG). The Classroom Exo uses a popular and well-accredited sEMG sensor called the Myoware sensor as shown in \autoref{fig:fig10}, which is easy to use and interface with the microcontroller and comes with a built-in filtering system that transforms raw EMG signal into usable readings (enveloped signal) \cite{AlTashi2024}.

\begin{figure}
	\centering
	
	\caption{Sensor Layout - MyoWareTM Muscle Sensor (AT-04-001) \cite{Myoware}.}
	\label{fig:fig11}
\end{figure}

The Classroom Exo implements a threshold-based control system using two MyoWare muscle sensors integrated with the PCB. The current system can accommodate two sEMG sensors connected to the PCB via insulated AUX cables (a 2-channel EMG control system). Each muscle sensor has two electrodes and a reference electrode \cite{AlTashi2024}. The sensor should be placed on the muscle intended to control the exoskeleton (here, the biceps/triceps brachii), and the reference electrode (preferably a bony part on your elbow). The muscle electrical activity can be broken down as follows: when you flex your arm, the biceps contract, and when you extend your arm, your triceps contract. 

\begin{figure}
	\centering
	
	\caption{Representation of the EMG signal before and after passing it through the sensor [4].}
	\label{fig:fig12}
\end{figure}

The electrode placement as shown in \autoref{fig:fig12}, is pivotal to getting steady and strong signals. These arm movements in turn control the servo movements in the hardware. When the amplitude of the EMG signal exceeds a set threshold, the servo motor contracts the arm of the exoskeleton. When the amplitude of the EMG signal goes under a set lower threshold, the servo motor of the exo moves in the other direction thus extending the arm. We can monitor the amplitude of the enveloped signals in real-time graphs on the MATLAB GUI and manually set the threshold values. 

\begin{figure}
	\centering
	
	\caption{Electrode Placement and Muscle Anatomy \cite{Muscles}. }
	\label{fig:fig13}
\end{figure}

\newpage
\subsection{EMG setup}
The exoskeleton should be put on before attaching the sEMG sensor. 
1.	Take out the sEMG sensors and three surface electrodes from the plastic bag.
2.	Attach the surface electrodes (before removing them from the plastic) to the EMG sensors \autoref{fig:fig14}. 

\begin{figure}[H]
	\centering
	
	\caption{Attaching the surface electrodes to the sensor.}
	\label{fig:fig14}
\end{figure}

3.	Attach the EMG sensor to the bicep and plug the AUX cable into the Classroom Exo to channel zero or one \autoref{fig:fig15}.  

\begin{figure}[H]
	\centering
	
	\caption{Placing the EMG sensor on the bicep and plugging in the AUX cable to the preferred channel.}
	\label{fig:fig15}
\end{figure}

4.	Attach the reference cable (red one) on the bony part of the elbow with a surface electrode on it \autoref{fig:fig16}.  

\begin{figure}[H]
	\centering
	
	\caption{Placing the reference cable on the elbow.}
	\label{fig:fig16}
\end{figure}

5.	As shown in \autoref{fig:fig17}, choose the tab “EMG control” in the GUI. 

\begin{figure}[H]
	\centering
	
	\caption{Choosing the EMG control tab.}
	\label{fig:fig17}
\end{figure}

6.	In the drop-down menu, choose the EMG channel selected when you plugged in the EMG sensor to the Classroom Exo.  
\begin{figure}[H]
	\centering
	
	\caption{Choosing the EMG channel.}
	\label{fig:fig18}
\end{figure}

7.	Before you click on start, you can control if the EMG sensor is on by checking if the little lights in the EMG sensor are blinking. It should blink green if it has power, and red if it detects muscle activity as observed in \autoref{fig:fig19}. 

\begin{figure}[H]
	\centering
	
	\caption{Lighhts corresponding to power and muscle potential on the eMG sensor.}
	\label{fig:fig19}
\end{figure}

8.	Click on the start button. 
9.	If you can see the curve changing when flexing your muscle, but the Classroom Exo does not move, then you can stop running and adjust the threshold. This is done by dragging the mark along the bar with numbers below the Threshold title at the bottom of the GUI as in \autoref{fig:fig20}. You can change both the upper and lower thresholds. 

\begin{figure}[H]
	\centering
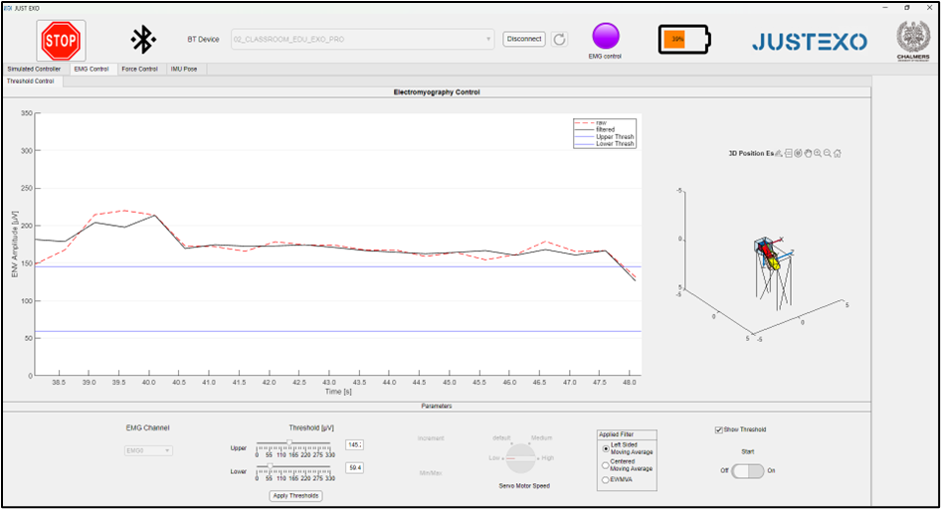
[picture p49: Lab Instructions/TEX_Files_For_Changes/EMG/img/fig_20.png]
	
	\caption{Adjusting the threshold in the GUI.}
	\label{fig:fig20}
\end{figure}

\newpage
\section{Exercises}
This section outlines a series of exercises to be completed during the allotted lab time. These exercises are designed to deepen your understanding of how EMG control can be applied in combination with the Classroom Exo. 

\subsection{Tasks and questions}

\begin{enumerate}[]
	\item Flex your bicep, if the EMG signal exceeds the upper threshold, you should see the exoskeleton move.  
	\begin{enumerate}[]
		\item Disconnect the reference electrode. Do you notice any difference from before, why? 
		\item Change the position of the reference electrode to: 
		\begin{enumerate}[]
			\item the same muscle as the body of the sensor (the bicep)
			\item a muscle in the opposite arm. Do you notice a difference, why? 
			\textbf{Reposition the reference electrode to the bony part after this exercise.}
		\end{enumerate}
	\end{enumerate}
\end{enumerate}
 
\begin{enumerate}[]
	\item Flex your bicep, if the EMG signal exceeds the upper threshold, you should see the exoskeleton move.  
	\begin{enumerate}[]
		\item Try different sensor positions:  
		\begin{enumerate}[]
			\item Rotate the sensor 180 degrees to change its orientation. 
			Do you see any alterations in the output signal? Why/why not? 
			\item Move the electrodes farther away from the central part of the target muscle. 
			How does the signal strength/quality change? 
		\end{enumerate}
	\end{enumerate}
\end{enumerate}
	
\begin{enumerate}[]
	\item What are the default threshold limits?  
	\begin{enumerate}[]
			\item Lower both thresholds, click “apply thresholds” and restart the start button. 
			\item What does controlling the exoskeleton feel like now? 
			\item What would the applications be for lowering the limits? 
			\textbf{Revert to the default threshold limits after the exercise.} 
	\end{enumerate}
\end{enumerate}

\begin{enumerate}[]
	\item 	When the sensor is on, try different movements: 
	\begin{enumerate}[]
		\item Move your arm around instead of extending or flexing it. What changes do you observe with the signal? 
		\item Walk around while still wearing the exoskeleton. What changes do you observe with the signal during these movements? 
		\item How can we describe what you observe in terms of disturbance signals (external factors like the environment, body movement, etc.) and sensitivity of the sensor? 	
	\end{enumerate}
\end{enumerate}

\begin{enumerate}[]
	\item Try different muscles:
	\begin{enumerate}[]
		\item Switch to a different muscle (this might be easier if you remove the exo from your body). Try using a larger or smaller muscle, for example, Gastrocnemius (the calf), etc. 
		\begin{figure}
			\centering
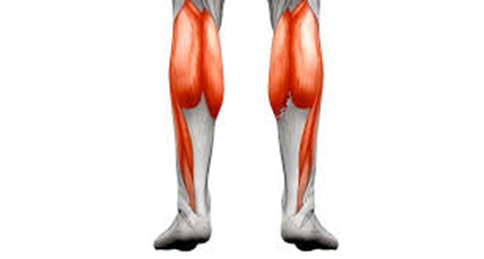
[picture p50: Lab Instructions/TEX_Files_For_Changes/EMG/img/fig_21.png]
			
			\caption{Try placing the sensor on the calf muscle instead of the Biceps \cite{Walden2022}.}
			\label{fig:fig21}
		\end{figure}
		\item Observe and note how high the muscle activity is in each of your target muscles. 
		\item What would be the application of controlling an exoskeleton with another muscle? For example, what would be a real-life application to use the calf muscle to control elbow flexion in an upper body exoskeleton? 
	\end{enumerate}
\end{enumerate}

\begin{enumerate}[]
	\item Dual Channel: Connect one of the EMG sensors to the Biceps (say EMG0), and the other to the Triceps (say EMG1). Click on the dual button to activate both channels. Note that each channel now corresponds to one of the thresholds and the servo changes direction if it crosses the upper or lower thresholds. 
\end{enumerate}

\begin{figure}
	\centering
	
	\caption{Choosing the dual channel mode. }
	\label{fig:fig22}
\end{figure}

Flex your bicep. If  EMG0 exceeds the upper threshold, you should see the exoskeleton move, and as you relax, and EMG1 exceeds the lower threshold you should see the exoskeleton extend as well. 
\begin{enumerate}[]
	\item How are the mono and dual modes different from each other? Do you see anyone having an advantage over another? 
	\item How can these two modes be deployed in real-life applications of the exoskeleton and more? 
\end{enumerate}
 
\subsection{Discussion}
For the best learning experience, feel free to discuss the results your group obtained from each step between groups to gain understanding and new perspectives.

\begin{enumerate}[]
	\item What differed between your answers and the answers of other groups?
	\item Why did your answers or conclusions differ?
	\item Did your discussions between groups lead to new insights or ideas? If so, what were they?
\end{enumerate}

\section{Typical Errors and Troubleshooting}
In this section, we present typical errors and issues encountered during testing of the Classroom Exo.

\begin{enumerate}[]
	\item If the EMG does not start (green lights start blinking) try changing the EMG sensor or channel. You could also try wiping the area where the electrodes are placed with a wet wipe before putting the sensor on the skin. 
	\item If the thresholds are not showing or the signal is not showing after changing the thresholds, then click “apply thresholds” and turn the start button off and then on again. Wait for the signal to appear. 
	
\end{enumerate}	
	 
\begin{figure}[H]
	\centering
	
	\caption{Steady signal corresponding to having chosen the wrong EMG channel. }
	\label{fig:fig23}
\end{figure}

\begin{enumerate}[]
	\setcounter{enumi}{2}
	\item If nothing happens when you flex your muscle, and the signal does not change: 
	\begin{enumerate}[]
		\item Make sure the sensor is intact on the arm. 
		\item Check if the EMG is actually powered (the green light should be on), if it receives signals the red light should be blinking. 
		\item Check your connections with the AUX cable to the exo, and the sensor wires. A loose connection could be causing trouble. 
		\item Switch to a different sensor if the issue persists. 
	\end{enumerate}
	\item If you are having trouble with the EMG signal for example steady low/steady high signal, try checking the connection with the aux cable and the connection with the electrodes (push it in). 
	\item When the person who is wearing the electrode touches a computer at the same time as the GUI runs, the signal might be erratic and unsteady. 
	\item If you get a constant and steady signal, maybe you have chosen the wrong channel.
\end{enumerate}

\begin{tcolorbox}[colback=green!5!white,colframe=green!75!black,title=Hint]
	You can find a more comprehensive Troubleshooting documentation in the Manual on our GitHub!
\end{tcolorbox}
\vspace{0.5cm}

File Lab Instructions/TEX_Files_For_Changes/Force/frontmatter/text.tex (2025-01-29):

% !TeX spellcheck = en_US
%\setcounter{chapter}{6} % set chapter counter so we begin at chapter 5
%\chapter{Laboration: PI/PID control of The Classroom Exo}

\section{Lab Introduction}

\begin{tcolorbox}[colback=blue!5!white,colframe=blue!75!black,title=Summary]
	In this chapter you will find the necessary documentation to setup your Classroom Exo, and try out the Force options. We have prepared some Lab exercises, to help you learn more about the force control options!
\end{tcolorbox}
\vspace{0.5cm}

An exoskeleton is a wearable mechanical structure that enhances or restores the physical abilities of the wearer by providing external support or amplification of movements \cite{AlTashi2024}. As the field of robotics grows leaps and bounds with every passing day as the world of STEM aims to integrate technology with humans to aid and support or enhance activities of daily living. Education leveraging these technologies has however been lacking. 
This lab is intended for use at a university level and is a derivative of a project aimed at converting an open-source exoskeleton into educational material \cite{AlTashi2024}. The Classroom Exo, the product that we will be using through the course of this lab, is a student-friendly optimized version of the EduExo Pro - An Advanced Robotic Exoskeleton Kit developed by Auxivo AG. 

\subsection{Risk section}
The Classroom Exo is not categorized as a medical device. Instead, its primary focus is educational. It is designed to provide hands-on experience with various control systems. There are some risks associated with the use of the Classroom Exo. Listed below are the potential risks, what has been done to prevent them, and the possible causes of these risks.
\begin{itemize}[]
	\item \textbf{Muscle fatigue:} Muscle fatigue can occur during prolonged use, as the Classroom Exo is somewhat heavy. To minimize this risk, an ergonomic design and proper usage guidelines have been implemented.
	\item \textbf{Injury risk:} The risk of injury is very low, but it still exists. The primary cause is misalignment between the Classroom Exo's mechanical joints and the user's shoulder and elbow joints. This risk has been minimized through proper calibration, an emergency stop feature, and clear instructions for how to put on the Classroom Exo.
\end{itemize}

\subsection{Learning objectives}
The goal of this lab is to provide hands-on experience with the Classroom Exo as a practical example of applying engineering principles within the biomedical field. Throughout the lab, you will explore how force sensors can be used to control an exoskeleton. By experimenting with different thresholding levels you will consider the practical applications of force-controlled exoskeletons, understanding how and why they are used in different scenarios. By the end of this lab you should be able to:

\begin{itemize}[]
	\item Implement force control on an exoskeleton and adjust threshold settings.
	\item Explain how threshold settings influence exoskeleton movement, and analyze its impact on performance and safety. 
	\item Evaluate the practical applications for this control method in terms of use case and user safety.	
\end{itemize}

\subsection{Prerequisite knowledge}
There is no specific prerequisite knowledge required for this lab. Any student group interested in product design, user safety, or gaining insight into biomedical engineering principles can benefit from this lab. However, due to the complexity of the system, the use of MATLAB, and potential troubleshooting, this lab may be most suitable for engineering students.

\subsection{Materials and methods}
For this lab, you will need a Bluetooth-enabled computer and MATLAB 2023b (although newer versions should also work). We will be interfacing with the exoskeletons using the “Updated BT-GUI” MATLAB application. Additionally, you will need one exoskeleton and a 2.5 and 3,0 Allen Key to adjust the arm length of the exoskeleton to fit the anatomy of the student who will be wearing the exoskeleton. 

\subsection{To do at home before the lab}
To make the most of the limited time you will have with the exoskeletons, you must come to the lab session well-prepared. Unforeseen issues or complications with the setup of the exoskeletons may arise, so proper preparation will ensure you have as much hands-on time as possible with the exoskeleton. Therefore before the lab asks you to:  
\begin{enumerate}[]
	\item Download MATLAB 2023b.
	\item Download the “Updated BT-GUI\_10-24”  folder from the GitHub link: \url{https://github.com/fabianjust/classroom-exo}
	\item Download and install the following MATLAB packages: 
	\begin{itemize}[]
		\item Control System Toolbox (version 23.2)
		\item Instrument Control Toolbox (version 23.2)
		\item Robotics System Toolbox (version 23.2)
		\item Sensor Fusion and Tracking Toolbox (version 23.2)
		\item Signal Processing Toolbox (version 23.2)
		\item Symbolic Math Toolbox (version 23.2)
	\end{itemize}
	\item Read the lab PM thoroughly.
\end{enumerate}

\newpage

\section{Introduction to the Exoskeleton}
Exoskeletons are increasingly being incorporated into rehabilitative settings, such as walking assists for people who have undergone spinal cord injuries, strokes, etc., in physiotherapy, and occupational therapy \cite{Hill2017}. Although aimed to be used in educational settings only, the Classroom Exo is an exoskeleton connected to the upper part of the body, over the shoulder, and the upper and lower arm, with a spring support to help lift the arm \autoref{fig:fig02}. Programmed on Arduino, it has three control systems - proportional–integral–-derivative controller (PID Controller), Electromyography signals from the muscles, and a force sensor on the wrist, the software of which is accessible as open-source, with a classroom-friendly graphical interface implemented on MATLAB. 

\begin{figure}[H]
	\centering
	
	\caption{The Classroom Exo and its adaptations from EduExo Pro }
	\label{fig:fig02}
\end{figure}

\subsection{Setting up the Classroom Exo}
While putting on the exoskeleton it is helpful if one person holds it up and another tightens the straps.
\begin{enumerate}[]
	\item Put on the vest and fasten the buckles. 
	\item Make sure that the shoulder part of the exoskeleton is aligned with your shoulder, which can be seen in \autoref{fig:fig03}. And then tighten the chest and waist straps.
\end{enumerate}

\begin{figure}[H]
	\centering
	
	\caption{Shoulder joint aligned (left) and misaligned (right).}
	\label{fig:fig03}
\end{figure}

\begin{enumerate}[]
	\setcounter{enumi}{2}
	\item Tighten the straps around the elbow and the wrist and check alignment with the elbow joint according to \autoref{fig:fig04}. 
\end{enumerate}

\begin{figure}[H]
	\centering
	
	\caption{Correct alignment of elbow joint (left) and incorrect alignment (right), misalignment marked in red.}
	\label{fig:fig04}
\end{figure}

\begin{enumerate}[]
	\setcounter{enumi}{3}
	\item If the Classroom Exo has the correct joint alignment as seen in figure 4 and 3, proceed to section 2.1.2. If not, proceed with section 2.1.1 “Adjusting the exoskeleton”.
\end{enumerate}

\subsubsection{Adjusting the exoskeleton}
To be able to adjust the arm length of the Classroom Exo, a 2.5 and 3.0 Allen Key is needed.

\begin{enumerate}[]
	\item Under the shoulder joint on the back of the exoskeleton you can find two bolts for which the 3.0 Allen Key fits, the bolts are marked in \autoref{fig:fig05}. Loosen these, align shoulder joints according to \autoref{fig:fig03} and tighten the bolts. 
\end{enumerate}

\begin{figure}[H]
	\centering
	\begin{center}
		\begin{tikzpicture}
			\node(a){};
			\node at(a.center)[draw, red,line width=3pt,circle, minimum width=45pt, minimum height=45pt,rotate=-40,yshift=-65pt]{};
		\end{tikzpicture}   
	\end{center}
	\caption{Bolts for adjusting shoulder breadth in red.}
	\label{fig:fig05}
\end{figure}

\begin{enumerate}[]
	\setcounter{enumi}{1}
	\item To align the elbow, loosen the bolts on the inside of the shoulder joint illustrated in \autoref{fig:fig06}. Use the 3.0 Allen key to do this. Slide the arm such that the elbow joint of the exoskeleton and the user is aligned such as in \autoref{fig:fig04}. Tighten the bolts.
\end{enumerate}

\begin{figure}[H]
	\centering
	\begin{center}
		\begin{tikzpicture}
			\node(a){};
			\node at(a.center)[draw, red,line width=3pt,circle, minimum width=45pt, minimum height=45pt,rotate=0,yshift=-7pt, xshift=-1pt]{};
		\end{tikzpicture}   
	\end{center}
	\caption{Bolts to adjust upper arm length for elbow alignment marked in red.}
	\label{fig:fig06}
\end{figure}

\begin{enumerate}[]
	\setcounter{enumi}{2}
	\item To adjust the position of the wrist cuff, loosen the bolt on the lower part on the arm of the exoskeleton marked in \autoref{fig:fig07}, using the 2.5 Allen key. Adjust length and tighten the bolts.
\end{enumerate} 

\begin{figure}[H]
	\centering
	\begin{center}
		\begin{tikzpicture}
			\node(a){};
			\node at(a.center)[draw, red,line width=3pt,circle, minimum width=15pt, minimum height=15pt,rotate=0,xshift=-12pt, yshift=-2pt]{};
		\end{tikzpicture}   
	\end{center}
	\caption{Bolts to adjust lower arm length for positioning of wrist cuff marked in red.}
	\label{fig:fig07}
\end{figure}
\subsubsection{Connecting to the device and starting the GUI}
\begin{enumerate}[]
	\item Turn on the exoskeleton by pushing the “LED push button on PCB” as seen in \autoref{fig:fig08}. It  should blink blue indicating that it is searching for a Bluetooth device.
	\item When you are connecting to the exoskeleton for the first time, go to your computer's Bluetooth settings and add a Bluetooth device. When pairing, the name of your device will be XX\_CLASSROOM\_EDU\_EXO\_PRO where the XX is a number between 01 to 08 depending on which exoskeleton you have.
\end{enumerate}

\begin{figure}[H]
	\centering
	
	\caption{Pairing to a Bluetooth device for the first time.}
	\label{fig:fig08}
\end{figure}
\begin{enumerate}[]
	\setcounter{enumi}{2}
	\item In your computer's display settings set the screen size to 100\%.
\end{enumerate}
\begin{figure}[H]
	\centering
	
	\caption{Changing screen sizing.}
	\label{fig:fig09}
\end{figure}

\begin{enumerate}[]
	\setcounter{enumi}{3}
	\item Open MATLAB, locate the BT\_GUI file and double click on it. Or locate the file in your file explorer and select open with MATLAB. If you open the file in MATLAB’s app designer, click run.
	\item When the GUI is opened, choose the correct Bluetooth device, and click connect. 
\end{enumerate}

\begin{figure}[H]
	\centering
	
	\caption{Connecting to the Bluetooth device.}
	\label{fig:fig10}
\end{figure}

The power button on the exoskeleton and the indicator in the GUI should change color to either green, yellow or red depending on the battery level.

\newpage
\section{Force controller}
\subsection{Introduction}

Force control enables systems to detect and respond to external forces, making them adaptable to environmental changes or user force input \cite{Falkowski2024}. This concept is widely used across engineering, from rehabilitation to industrial applications \cite{Lang2022}. In rehabilitation, exoskeletons use force control to either assist in or add resistance to patients' intended motions \cite{Falkowski2024}. By using exoskeletons we can allow for movements that the patient otherwise could not perform, avoid over-extension, relieve physiotherapists' work burden, and gradually reduce the assistance as the patient regains strength \cite{Falkowski2024, Dickmann2021}.

Additionally, it might be useful in industrial settings for workers where the motor in the exoskeleton helps them in movements when the sensors detect forces or strains that would otherwise be harmful to the worker's body, thus preventing injuries \cite{Golabchi2022}. 

The Classroom Exo uses strain gauges at the wrist cuff to detect forces, see \autoref{fig:fig02}. When these sensors experience deformation due to a force, they change their resistance, altering the voltage over them \cite{AlTashi2024}. These sensors allow the exoskeleton to detect a voltage difference when an upward force exceeds a threshold and subsequently flex the elbow joint. Similarly, exceeding a downward threshold causes the elbow joint to extend, moving the arm to a straighter position.

\subsection{Force controller setup}
The exoskeleton should be put on before starting this part.

1.	Choose the “Force control” tab, and then the “Threshold” tab, which can be seen in \autoref{fig:fig11}.

\begin{figure}[H]
	\centering
	
	\caption{Choosing the force control tab (red) and the threshold tab (blue).}
	\label{fig:fig11}
\end{figure}

2.	At the bottom of the tab, you can see the force control parameters. Where you can change the upper and lower threshold force limits, the servo motor speed, and the applied filter. See \autoref{fig:fig12}.

\begin{figure}[H]
	\centering
	
	\caption{The tunable force control parameters.}
	\label{fig:fig12}
\end{figure}

3.	Ensure the “show threshold” box which you can see in \autoref{fig:fig12} is checked to see when the force on the wrist cuff exceeds the upper or lower threshold. 
4.	Click start. When trying out the force control by flexing and extending your arm you should see something like this:

\begin{figure}[H]
	\centering
	
	\caption{Force sensor data.}
	\label{fig:fig13}
\end{figure}

5.	When changing the threshold values, make sure to click “apply thresholds” and turn the start button off and then on again. 

\newpage
\subsection{Exercises}

\begin{tcolorbox}[colback=red!5!white,colframe=red!75!black,title=Attention]
	\textbf{OBS!} You can break pieces of the exoskeleton. Don’t try to exceed thresholds by more than necessary.
\end{tcolorbox}
\vspace{0.5cm}
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

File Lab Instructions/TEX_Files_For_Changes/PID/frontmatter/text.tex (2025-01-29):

% !TeX spellcheck = en_US
%\setcounter{chapter}{6} % set chapter counter so we begin at chapter 5
%\chapter{Laboration: PI/PID control of The Classroom Exo}

\section{Lab Introduction}

\begin{tcolorbox}[colback=blue!5!white,colframe=blue!75!black,title=Summary]
	In this chapter you will find the necessary documentation to setup your Classroom Exo, and try out the PI and PID controller options. We have prepared some Lab exercises, to help you learn more about control theory.
\end{tcolorbox}
\vspace{0.5cm}
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

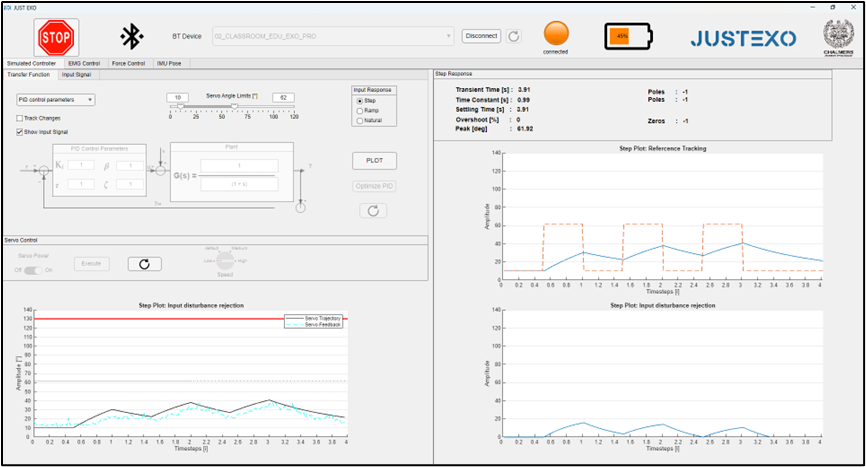
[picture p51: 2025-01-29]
Lab Instructions/TEX_Files_For_Changes/PID/img/fig_11.png

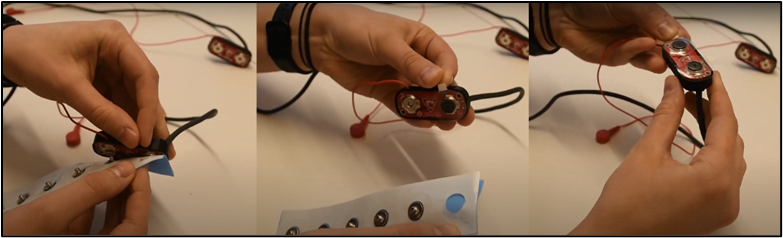
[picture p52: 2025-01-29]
Lab Instructions/TEX_Files_For_Changes/EMG/img/fig_14.png

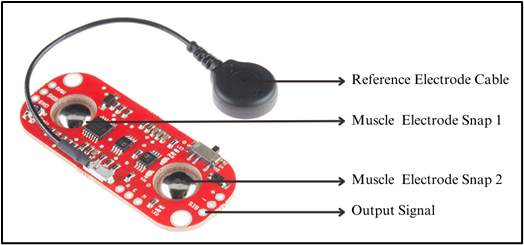
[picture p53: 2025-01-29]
Lab Instructions/TEX_Files_For_Changes/EMG/img/fig_11.png

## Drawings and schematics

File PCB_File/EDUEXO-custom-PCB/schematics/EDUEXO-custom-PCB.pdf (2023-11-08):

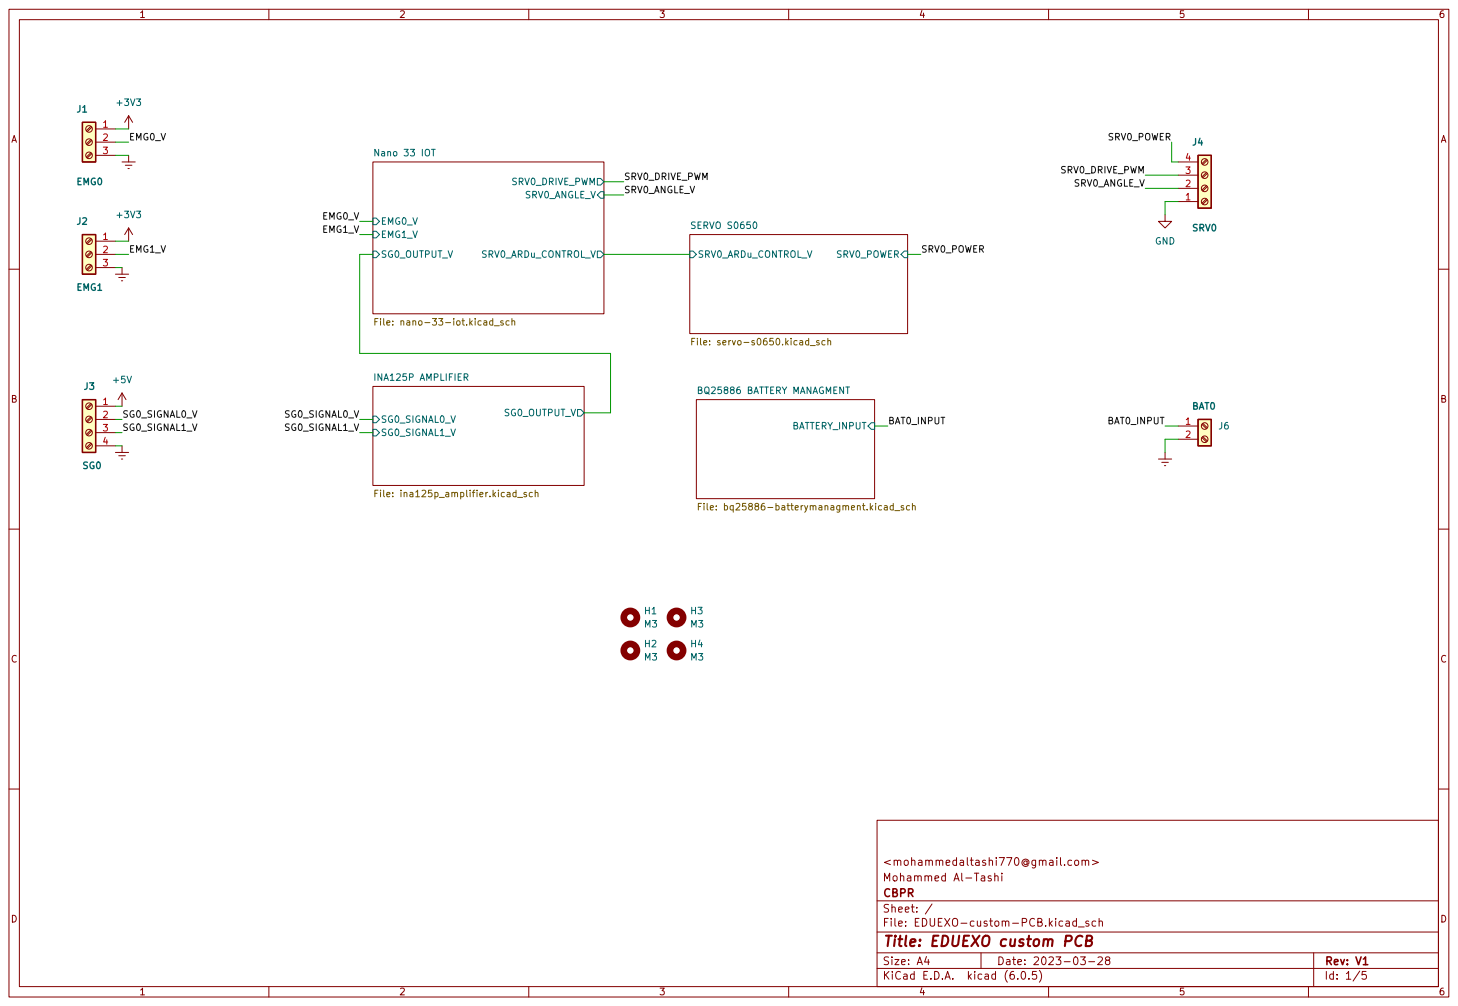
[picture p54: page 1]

SERVO S0650 File: servo-s0650.kicad_sch BATTERY_INPUT BQ25886 BATTERY MANAGMENT

File: EDUEXO-custom-PCB.kicad_sch Sheet: / CBPR Mohammed Al-Tashi <mohammedaltashi770@gmail.com>

Id: 1/5 Title: EDUEXO custom PCB

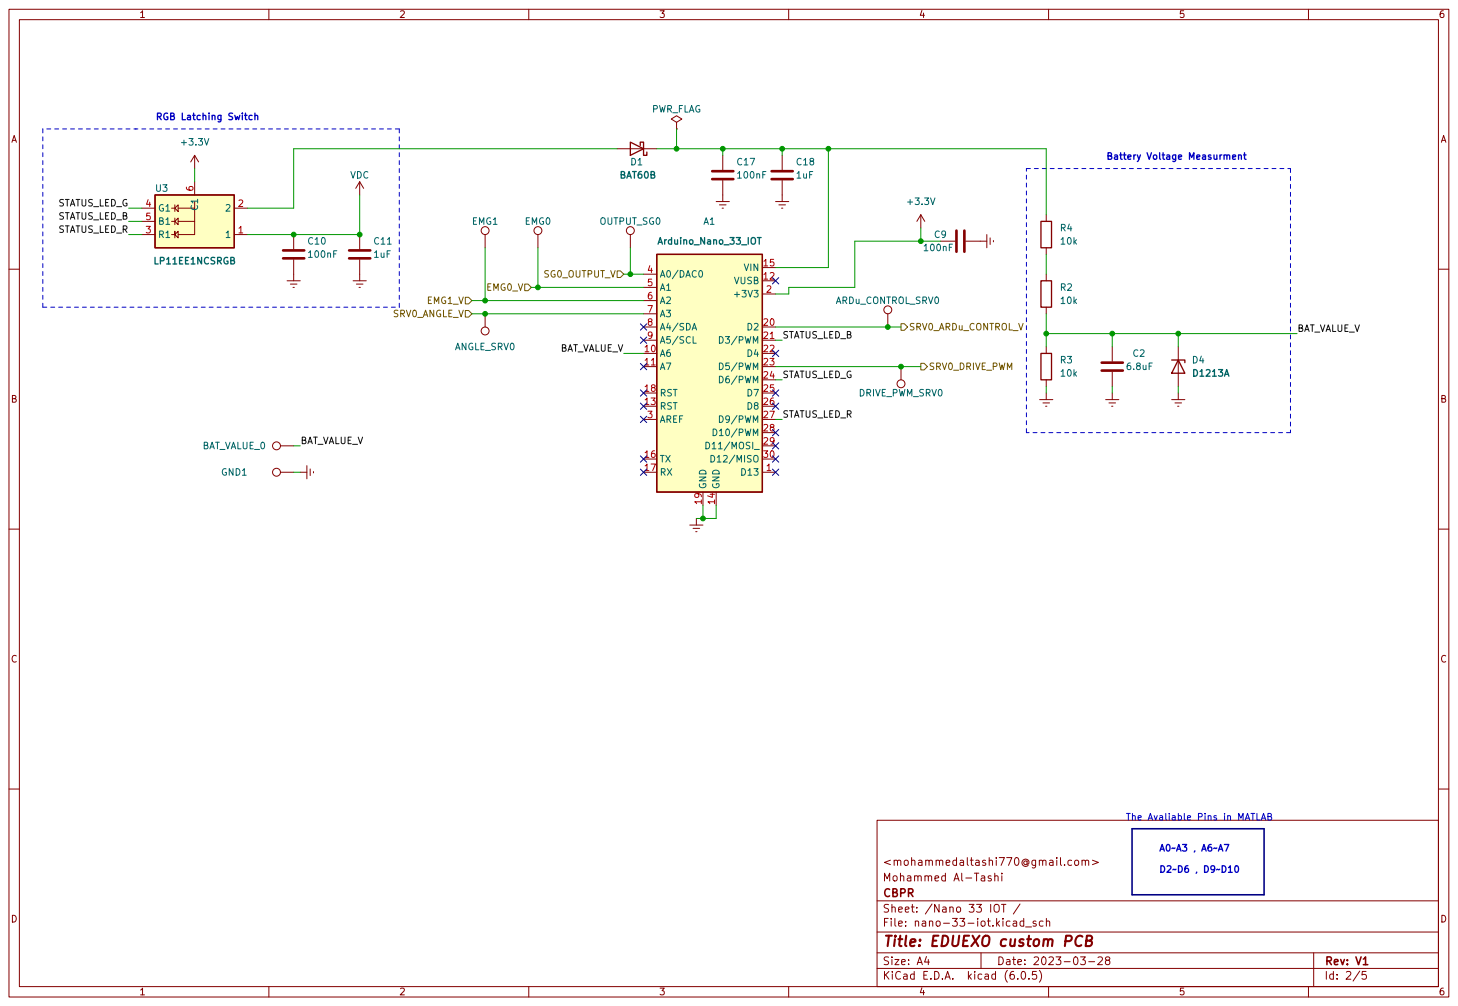
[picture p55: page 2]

A0~A3 , A6~A7 D2~D6 , D9~D10 The Avaliable Pins in MATLAB

File: nano-33-iot.kicad_sch Sheet: /Nano 33 IOT / CBPR Mohammed Al-Tashi <mohammedaltashi770@gmail.com>

Id: 2/5 Title: EDUEXO custom PCB

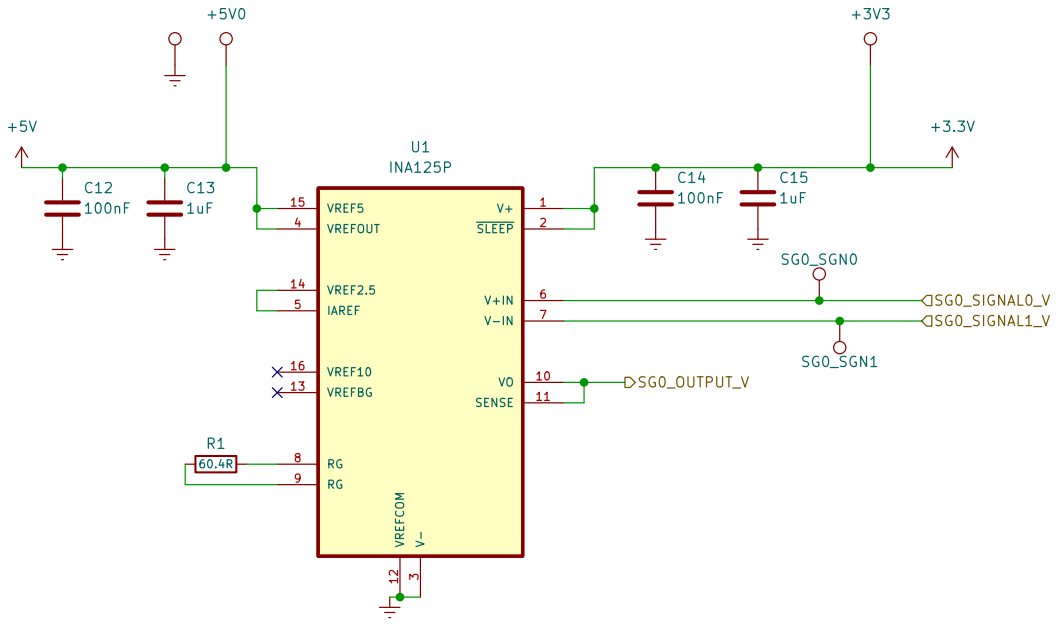
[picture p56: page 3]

File: ina125p_amplifier.kicad_sch Sheet: /INA125P AMPLIFIER/ CBPR Mohammed Al-Tashi <mohammedaltashi770@gmail.com>

Id: 3/5 Title: EDUEXO custom PCB

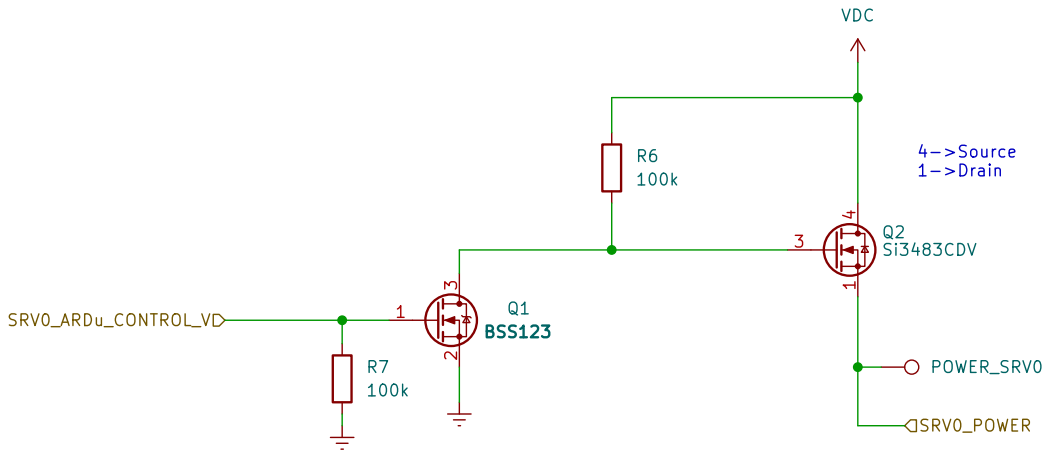
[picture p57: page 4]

File: servo-s0650.kicad_sch Sheet: /SERVO S0650/ CBPR Mohammed Al-Tashi <mohammedaltashi770@gmail.com>

Id: 6/5 Title: EDUEXO custom PCB

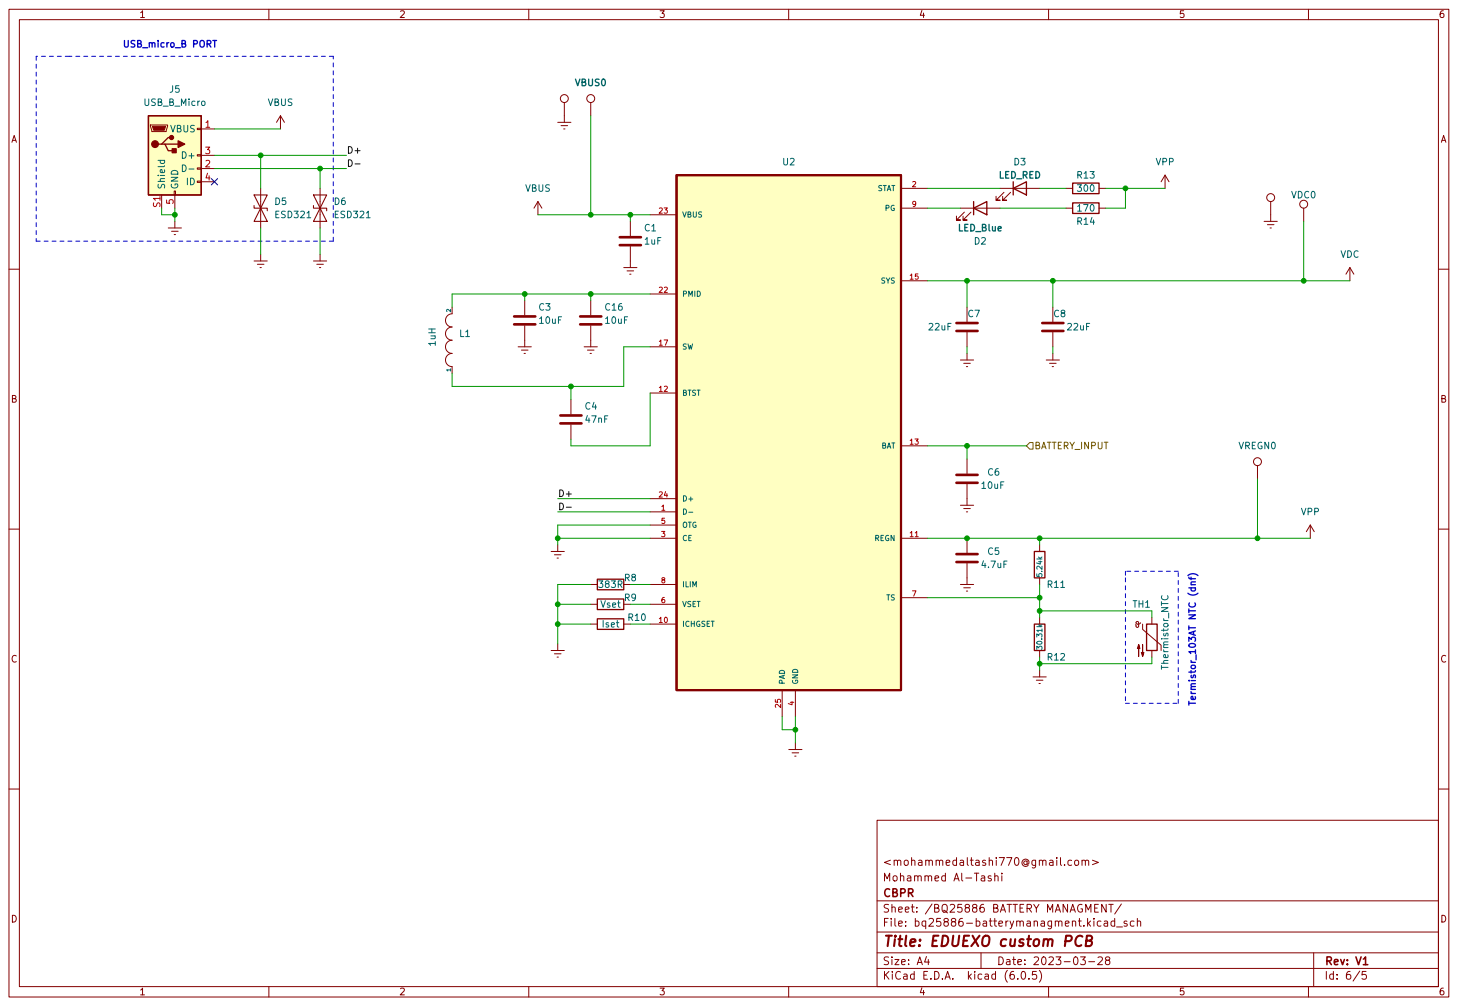
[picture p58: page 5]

Sheet: /BQ25886 BATTERY MANAGMENT/ CBPR Mohammed Al-Tashi <mohammedaltashi770@gmail.com>

File: bq25886-batterymanagment.kicad_sch
Id: 6/5 Title: EDUEXO custom PCB

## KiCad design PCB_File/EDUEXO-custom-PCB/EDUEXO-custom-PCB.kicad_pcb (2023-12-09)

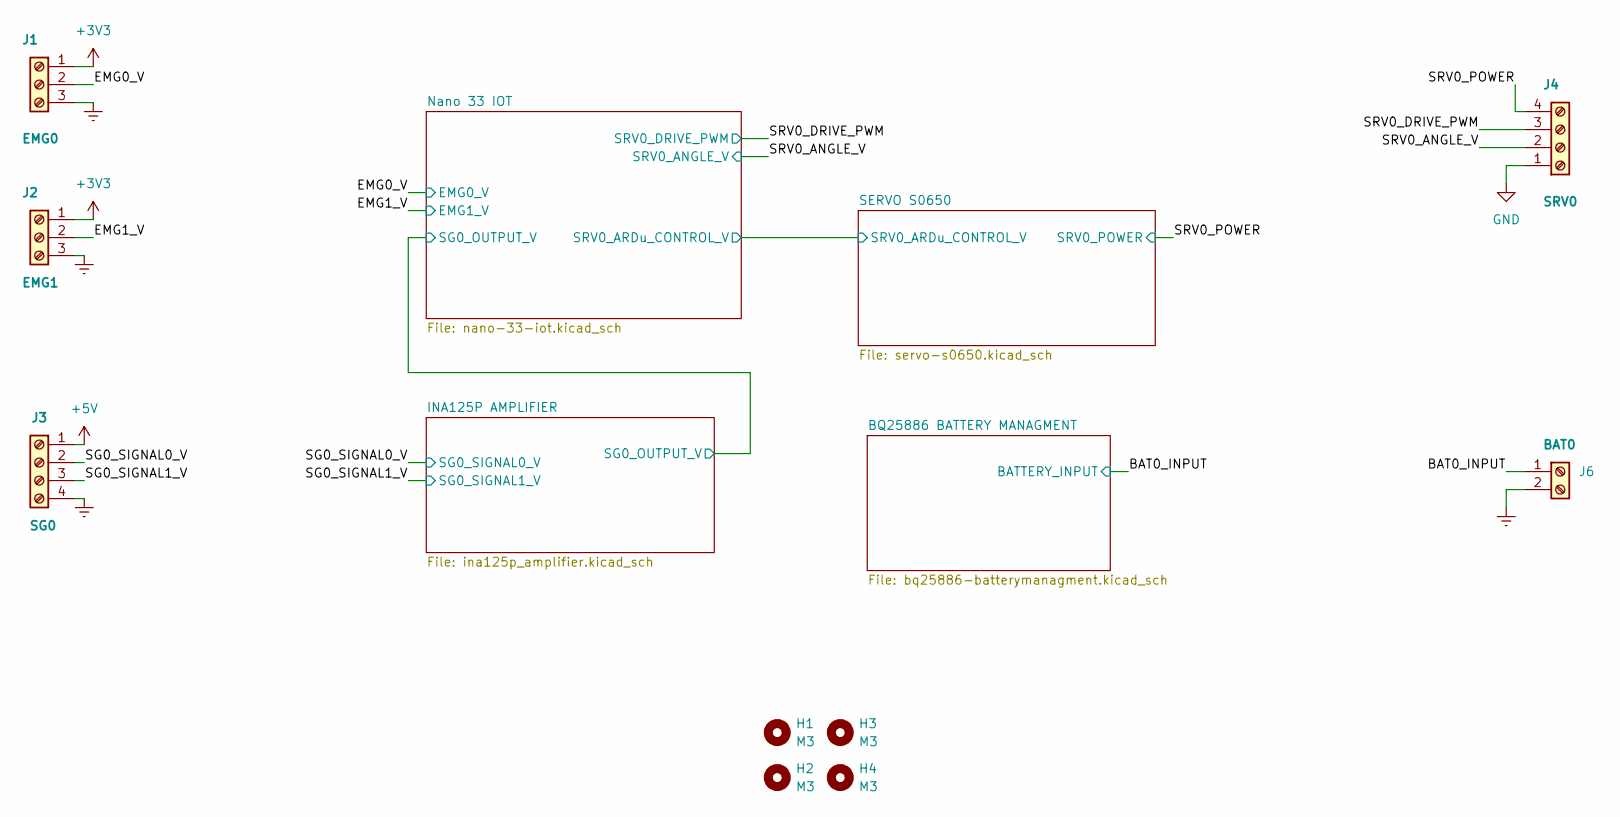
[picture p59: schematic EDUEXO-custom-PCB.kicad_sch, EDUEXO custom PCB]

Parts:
H1, H2, H3, H4: M3; MountingHole_3.2mm_M3
J1: EMG0; TE_1-2834011-3; MPN 1-2834011-3
J2: EMG1; TE_1-2834011-3; MPN 1-2834011-3
J3: SG0; TE_1-2834011-4; MPN 1-2834011-4
J4: SRV0; TE_1-2834011-4; MPN 1-2834011-4
J6: BAT0; TE_1-2834011-2; MPN 1-2834011-2

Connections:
+5V: J3.1; also elsewhere on the board
/BAT0_INPUT: J6.1; also elsewhere on the board
/EMG0_V: J1.2; also elsewhere on the board
/EMG1_V: J2.2; also elsewhere on the board
/SG0_SIGNAL0_V: J3.2; also elsewhere on the board
/SG0_SIGNAL1_V: J3.3; also elsewhere on the board
/SRV0_ANGLE_V: J4.2; also elsewhere on the board
/SRV0_DRIVE_PWM: J4.3; also elsewhere on the board
/SRV0_POWER: J4.4; also elsewhere on the board

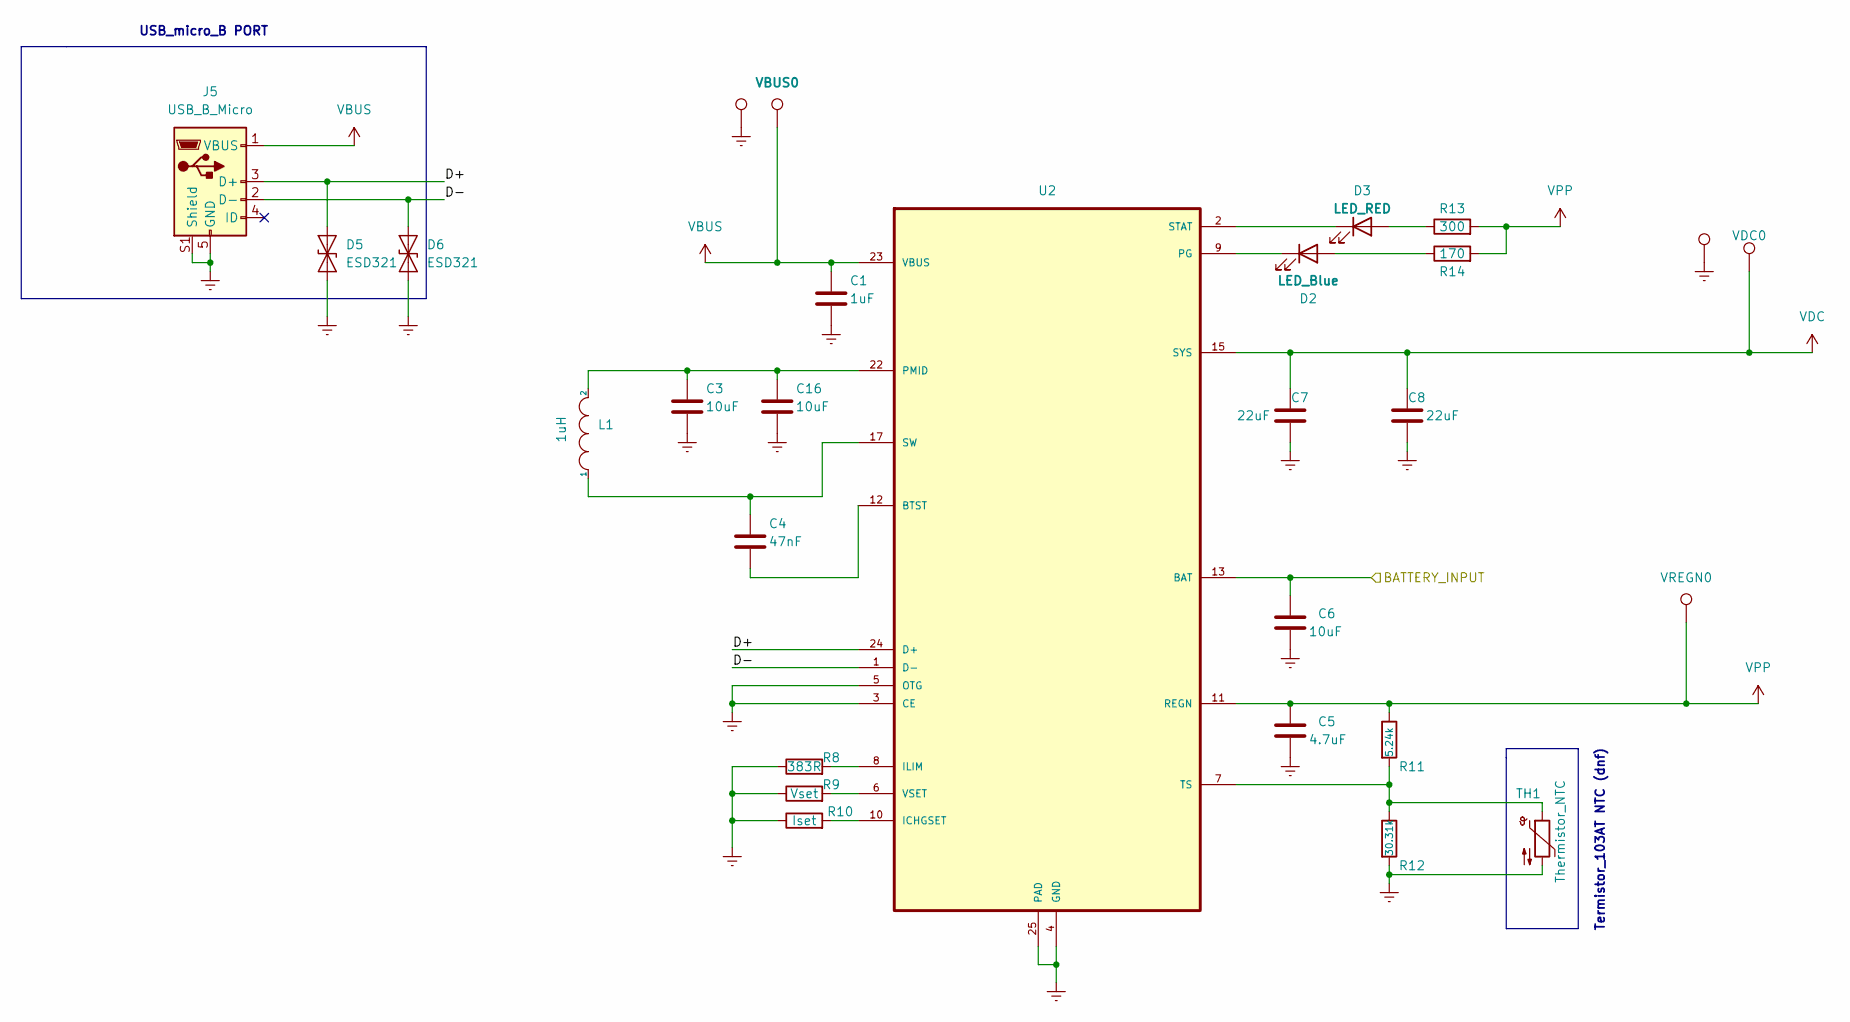
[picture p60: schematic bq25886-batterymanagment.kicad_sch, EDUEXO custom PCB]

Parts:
C1: 1uF; C_0805_2012Metric; MPN C2012X7R1H105K125AB
C3, C6, C16: 10uF; C_0805_2012Metric; MPN C2012X5R1E106K125AB
C4: 47nF; C_0805_2012Metric; MPN C2012X7T2W473K125AA
C5: 4.7uF; C_0805_2012Metric; MPN C2012X5R1E475K125AB
C7, C8: 22uF; C_0805_2012Metric; MPN C2012X5R1V226M125AC
D2: LED_Blue; LED_0603_1608Metric; MPN LTST-C191TBKT
D3: LED_RED; LED_0603_1608Metric; MPN LTST-C191KRKT
D5, D6: ESD321; D_0402_1005Metric; MPN ESD321DPYR
GND2, GND4: TestPoint; TestPoint_Keystone_5000-5004_Miniature; MPN 5002
J5: USB_B_Micro; USB_micro_B_10118192-0002LF; MPN 10118192-0002LF
L1: 1uH; L_0630CDMCCDS-1R5MC; MPN 0630CDMCCDS-1R5MC
R8: 383R; R_0805_2012Metric; MPN RC0805FR-07383RL
R9: Vset; R_0805_2012Metric
R10: Iset; R_0805_2012Metric
R11: 5.24k; R_0805_2012Metric; MPN RC0805FR-075K23L
R12: 30.31k; R_0805_2012Metric; MPN RC0805FR-0730K1L
R13: 300; R_0805_2012Metric; MPN RC0805JR-07300RL
R14: 170; R_0805_2012Metric; MPN RC0805FR-07174RL
TH1: Thermistor_NTC; R_0805_2012Metric
U2: BQ25886RGER; Texas_S-PVQFN-N24_EP2.1x2.1mm_ThermalVias; MPN BQ25886RGER
VBUS0: TestPoint; TestPoint_Keystone_5000-5004_Miniature; MPN 5002
VDC0: TestPoint; TestPoint_Keystone_5000-5004_Miniature; MPN 5002
VREGN0: TestPoint; TestPoint_Keystone_5000-5004_Miniature; MPN 5002

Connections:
/BAT0_INPUT: C6.1, U2.13 (BAT), U2.14 (BAT); also elsewhere on the board
/BQ25886 BATTERY MANAGMENT/D+: D5.2 (A2), J5.3 (D+), U2.24 (D+)
/BQ25886 BATTERY MANAGMENT/D-: D6.2 (A2), J5.2 (D-), U2.1 (D-)
unnamed: C4.1, L1.1, U2.17 (SW), U2.18 (SW)
unnamed: C4.2, U2.12 (BTST)
unnamed: C3.1, C16.1, L1.2, U2.21 (PMID), U2.22 (PMID)
unnamed: D2.1 (K), U2.9 (PG)
unnamed: D2.2 (A), R14.1
unnamed: D3.1 (K), U2.2 (STAT)
unnamed: D3.2 (A), R13.1
unnamed: R8.2, U2.8 (ILIM)
unnamed: R9.2, U2.6 (VSET)
unnamed: R10.2, U2.10 (ICHGSET)
unnamed: R11.2, R12.1, TH1.1, U2.7 (TS)
VBUS: C1.1, J5.1 (VBUS), U2.23 (VBUS), VBUS0.1
VDC: C7.1, C8.1, U2.15 (SYS), U2.16 (SYS), VDC0.1; also elsewhere on the board
VPP: C5.1, R11.1, R13.2, R14.2, U2.11 (REGN), VREGN0.1

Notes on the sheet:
USB_micro_B PORT
Termistor_103AT NTC (dnf)

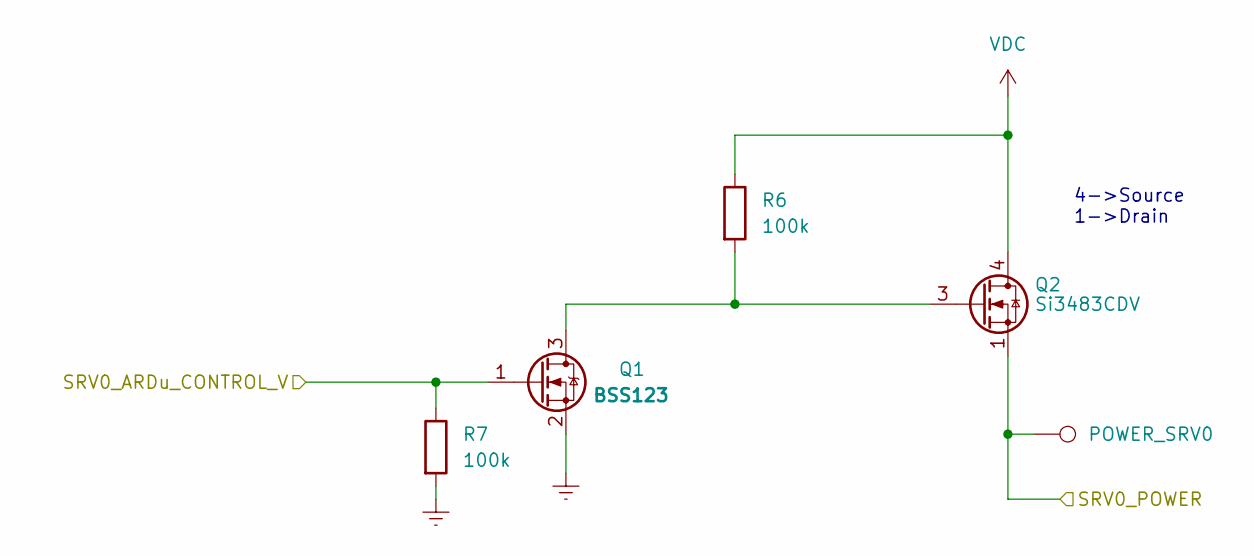
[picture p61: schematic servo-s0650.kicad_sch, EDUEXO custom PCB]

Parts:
POWER_SRV0: TestPoint; TestPoint_Keystone_5000-5004_Miniature; MPN 5002
Q1: BSS123; SOT-23; MPN BSS123
Q2: Si3483CDV; TSOT-23-6; MPN Si3483CDV
R6, R7: 100k; R_0805_2012Metric; MPN RC0805FR-13100KL

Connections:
/Nano 33 IOT /SRV0_ARDu_CONTROL_V: Q1.1 (G), R7.1; also elsewhere on the board
/SRV0_POWER: POWER_SRV0.1, Q2.1 (D), Q2.2 (D), Q2.5 (D), Q2.6 (D); also elsewhere on the board
unnamed: Q1.3 (D), Q2.3 (G), R6.2
VDC: Q2.4 (S), R6.1; also elsewhere on the board

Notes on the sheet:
4->Source 1->Drain

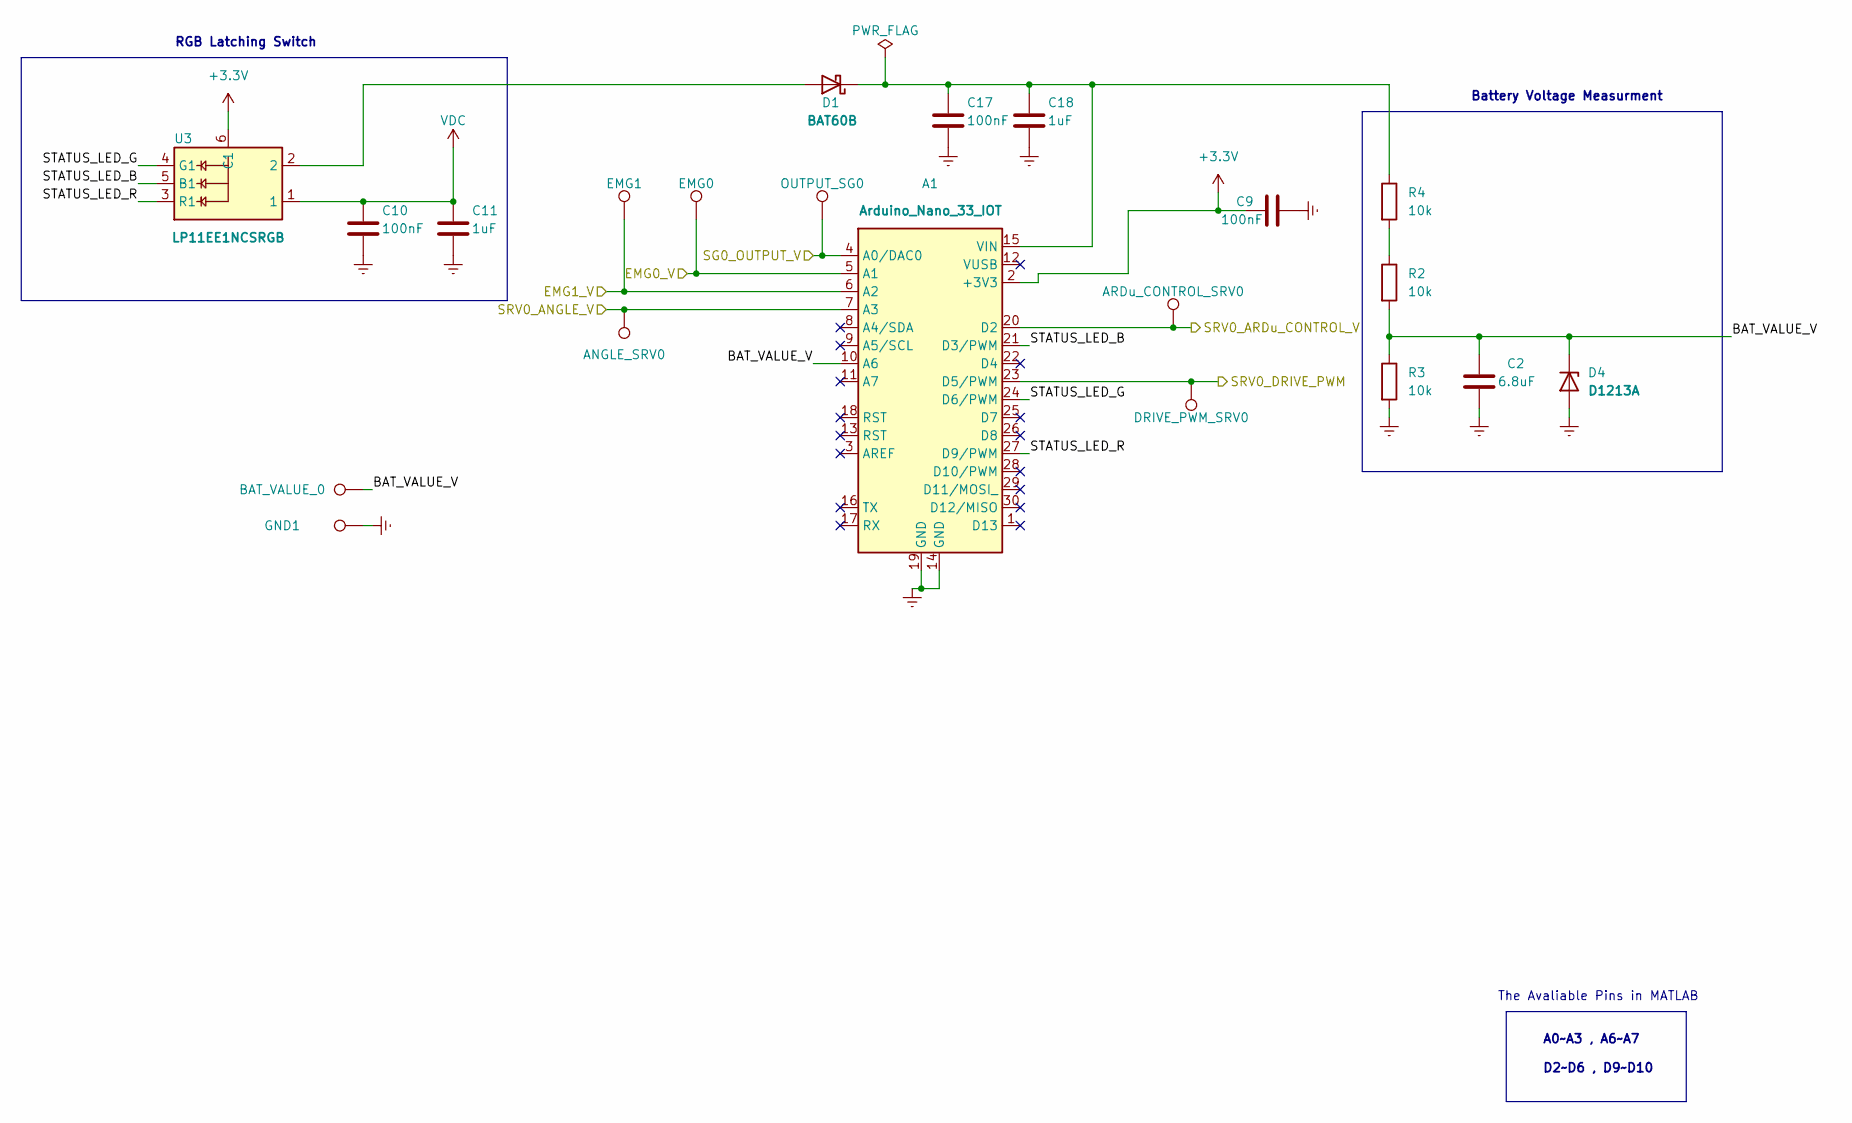
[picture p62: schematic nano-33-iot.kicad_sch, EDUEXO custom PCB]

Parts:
A1: Arduino_Nano_33_IOT; MODULE_ABX00027_ThroughHoles; MPN ABX00027
ANGLE_SRV0: TestPoint; TestPoint_Keystone_5000-5004_Miniature; MPN 5002
ARDu_CONTROL_SRV0: TestPoint; TestPoint_Keystone_5000-5004_Miniature; MPN 5002
BAT_VALUE_0: TestPoint; TestPoint_Keystone_5000-5004_Miniature; MPN 5002
C2: 6.8uF; C_0805_2012Metric; MPN C2012X8L0J685K125AC
C9, C10, C17: 100nF; C_0805_2012Metric; MPN C2012X7R2A104K125AA
C11, C18: 1uF; C_0805_2012Metric; MPN C2012X7R1H105K125AB
D1: BAT60B; D_SOD-323; MPN BAT60BE6327HTSA1
D4: D1213A; D_SOD-323; MPN D1213A-01WS-7
DRIVE_PWM_SRV0: TestPoint; TestPoint_Keystone_5000-5004_Miniature; MPN 5002
EMG0, EMG1: TestPoint; TestPoint_Keystone_5000-5004_Miniature; MPN 5002
GND1: TestPoint; TestPoint_Keystone_5000-5004_Miniature; MPN 5002
OUTPUT_SG0: TestPoint; TestPoint_Keystone_5000-5004_Miniature; MPN 5002
R2, R3, R4: 10k; R_0805_2012Metric; MPN RC0805JR-0710KL
U3: LP11EE1NCSRGB; SW_LP11EE1NCSRGB; MPN LP11EE1NCSRGB

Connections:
/EMG0_V: A1.5 (A1), EMG0.1; also elsewhere on the board
/EMG1_V: A1.6 (A2), EMG1.1; also elsewhere on the board
/INA125P AMPLIFIER/SG0_OUTPUT_V: A1.4 (A0/DAC0), OUTPUT_SG0.1; also elsewhere on the board
/Nano 33 IOT /BAT_VALUE_V: A1.10 (A6), BAT_VALUE_0.1, C2.1, D4.1 (K), R2.2, R3.1
/Nano 33 IOT /SRV0_ARDu_CONTROL_V: A1.20 (D2), ARDu_CONTROL_SRV0.1; also elsewhere on the board
/Nano 33 IOT /STATUS_LED_B: A1.21 (D3/PWM), U3.5 (B1)
/Nano 33 IOT /STATUS_LED_G: A1.24 (D6/PWM), U3.4 (G1)
/Nano 33 IOT /STATUS_LED_R: A1.27 (D9/PWM), U3.3 (R1)
/SRV0_ANGLE_V: A1.7 (A3), ANGLE_SRV0.1; also elsewhere on the board
/SRV0_DRIVE_PWM: A1.23 (D5/PWM), DRIVE_PWM_SRV0.1; also elsewhere on the board
unnamed: A1.15 (VIN), C17.1, C18.1, D1.1 (K), R4.1
unnamed: D1.2 (A), U3.2
unnamed: R2.1, R4.2
VDC: C10.1, C11.1, U3.1; also elsewhere on the board

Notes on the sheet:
A0~A3 , A6~A7 D2~D6 , D9~D10
The Avaliable Pins in MATLAB
RGB Latching Switch
Battery Voltage Measurment

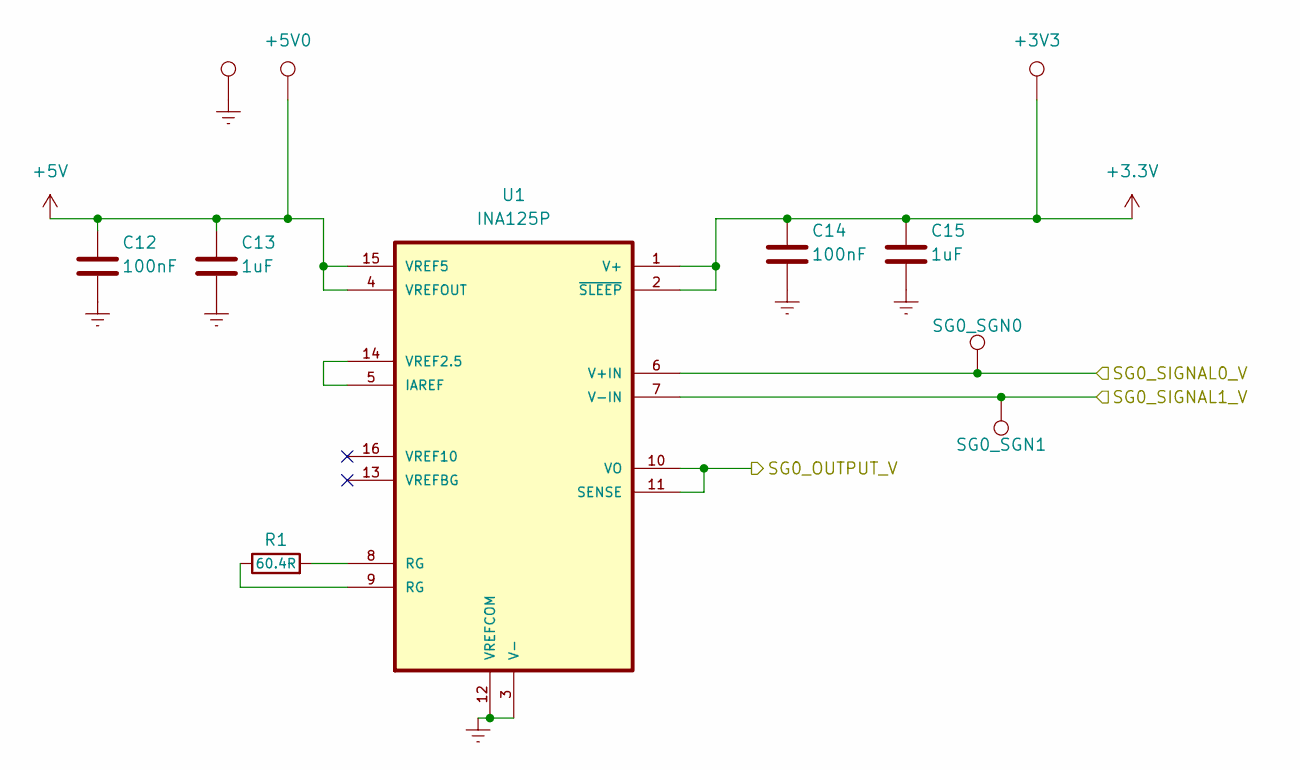
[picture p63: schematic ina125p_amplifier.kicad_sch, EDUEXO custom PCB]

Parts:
+3V3, +5V0: TestPoint; TestPoint_Keystone_5000-5004_Miniature; MPN 5002
C12, C14: 100nF; C_0805_2012Metric; MPN C2012X7R2A104K125AA
C13, C15: 1uF; C_0805_2012Metric; MPN C2012X7R1H105K125AB
GND3: TestPoint; TestPoint_Keystone_5000-5004_Miniature; MPN 5002
R1: 60.4R; R_0805_2012Metric; MPN RC0805FR-0760R4L
SG0_SGN0, SG0_SGN1: TestPoint; TestPoint_Keystone_5000-5004_Miniature; MPN 5002
U1: INA125P; DIP794W45P254L1969H508Q16; MPN INA125P

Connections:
+5V: +5V0.1, C12.1, C13.1, U1.4 (VREFOUT), U1.15 (VREF5); also elsewhere on the board
/INA125P AMPLIFIER/SG0_OUTPUT_V: U1.10 (VO), U1.11 (SENSE); also elsewhere on the board
/SG0_SIGNAL0_V: SG0_SGN0.1, U1.6 (V+IN); also elsewhere on the board
/SG0_SIGNAL1_V: SG0_SGN1.1, U1.7 (V-IN); also elsewhere on the board
unnamed: R1.1, U1.9 (RG)
unnamed: R1.2, U1.8 (RG)
unnamed: U1.5 (IAREF), U1.14 (VREF2.5)

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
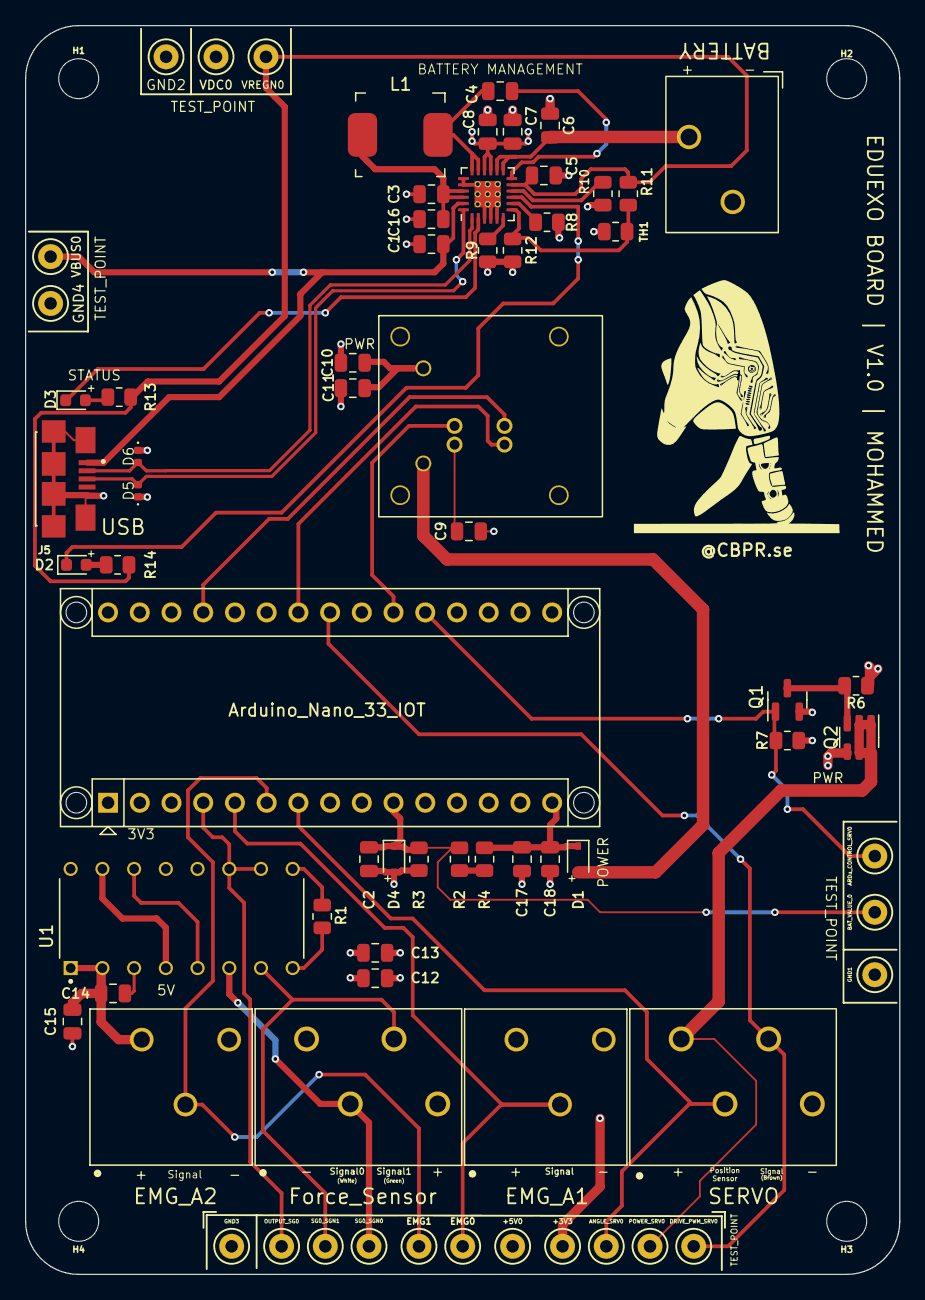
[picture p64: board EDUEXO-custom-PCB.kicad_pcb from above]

Board: 4 copper layers, 70.0 x 100.0 mm, 74 parts (0 on the bottom side), 40 nets.

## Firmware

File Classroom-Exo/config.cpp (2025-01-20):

#include "config.h"

// initialize message structs
message msg2send;
message msg2receive;

DeviceSettings currentSettings;

uint16_t current_servo_position = 1700;
uint16_t current_servo_micros = 2150;

String device_name = "";
bool dev_ok = false;
bool name_set = false;

uint8_t EMG0_SELECT_PIN = EMG_SENSOR0_PIN;
uint8_t EMG1_SELECT_PIN = EMG_SENSOR1_PIN;

// thresholds
int16_t forceThresholdUpper = 30;
int16_t forceThresholdLower = -30;
uint16_t emgThresholdUpper = 30;
uint16_t emgThresholdLower = 30;
uint16_t emgThreshold = 500;
uint8_t speed_setting = 1;
uint8_t angle_step = 10;
float gain = 0.1;

/**
 * @brief Initializes the hardware GPIO pins
 */
void initializeHardware() {
    // Set ADC resolution to 12 bit
    analogReadResolution(12);

    // Set up LED Pins
    pinMode(LED_PIN, OUTPUT);
    pinMode(RED_PIN, OUTPUT);
    pinMode(GREEN_PIN, OUTPUT);
    pinMode(BLUE_PIN, OUTPUT);

    // Set up Sensor Pins
    pinMode(EMG_SENSOR0_PIN, INPUT);
    pinMode(EMG_SENSOR1_PIN, INPUT);
    pinMode(FORCE_SENSOR_PIN, INPUT);

    // Set up Servo Motor Pins
    pinMode(SERVO_POSITION_PIN, INPUT);
    // pinMode(SERVO_CONTROL_PIN, OUTPUT);  // not necessary, since that is handled in the servo library!
    pinMode(SERVO_POWER_PIN, OUTPUT);
    
    #ifdef DEBUG
    Serial.println("GPIO Pins initialized  ");
    #endif

}

bool findDeviceSettings(const String& name, DeviceSettings& settings) {
  for (int i = 0; i < NUM_DEVICES; ++i) {
    if (name.equals(deviceSettingsArray[i].deviceName)) {
      settings = deviceSettingsArray[i];
      return true;
    }
  }
  return false;
}

void checkDeviceIntegrity() {
    if (dev_ok & !name_set) {
    Serial.println(device_name);
    delay(50);
    // Lookup the settings for the received device name
    if (findDeviceSettings(device_name, currentSettings)) {
#ifdef DEBUG
      Serial.print("Received device name: ");
      Serial.println(currentSettings.deviceName);
      Serial.println(device_name);
      Serial.print("Zero Servo Reference Bytes: ");
      Serial.println(currentSettings.servoZeroReferenceBytes);
      Serial.print("Ninety Servo Reference Bytes: ");
      Serial.println(currentSettings.servo110ReferenceBytes);
      Serial.print("Force Sensor Zero Reference: ");
      Serial.println(currentSettings.forceZeroReferenceValue);
#endif
      
      name_set = true;
    }
#ifdef DEBUG
    else {
      Serial.print("Error: Device name not recognized.   ");
      Serial.println(device_name);
      exit(0);
    }
#endif
  }
}

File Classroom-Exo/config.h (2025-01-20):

/**
 * @file config.h
 * @brief Configuration header file
 *
 * This file contains global variables and structures used across multiple modules, as well as Pin assignments and constants for the project
 */

#ifndef CONFIG_H
#define CONFIG_H

#define DEBUG
// #define DEBUG2
// #define DEBUG_BAT
#define SERVOMOVEMENT

#define BAUD_RATE 115200  ///< Serial communication baud rate
#define NINA_RESETN 6     ///< Reset pin for NINA module
#define MAX_DATA_LENGTH 200
#define NUM_CALIBRATION_POINTS 12

#include <Arduino.h>
#include <Servo.h>
#include <PID_v1.h>
#include "messaging_codes.h"
#include "control_modes.h"
#include "numeric_utils.h"


/// @brief Pin number for the onboard LED
const uint8_t LED_PIN = 13;

/// @brief Pin number for the red component of an RGB LED
const uint8_t RED_PIN = 9;

/// @brief Pin number for the green component of an RGB LED
const uint8_t GREEN_PIN = 6;

/// @brief Pin number for the blue component of an RGB LED
const uint8_t BLUE_PIN = 3;

/// @brief Pin number for servo control signal
const uint8_t SERVO_CONTROL_PIN = 5;

/// @brief Pin number for servo power control
const uint8_t SERVO_POWER_PIN = 2;

/// @brief Analog pin number for reading servo position
const uint8_t SERVO_POSITION_PIN = A3;

/// @brief Analog pin number for force sensor input
const uint8_t FORCE_SENSOR_PIN = A0;

/// @brief Analog pin number for the first EMG sensor input
const uint8_t EMG_SENSOR0_PIN = A1;

/// @brief Analog pin number for the second EMG sensor input
const uint8_t EMG_SENSOR1_PIN = A2;

/// @brief Pin number for EMG sensor selection
extern uint8_t EMG0_SELECT_PIN;

/// @brief Pin number for EMG sensor selection
extern uint8_t EMG1_SELECT_PIN;

/// @brief Analog pin number for battery voltage measurement
const uint8_t BATTERY_VOLTAGE_PIN = A6;

/// @brief Baud rate for serial communication
const uint16_t SERIAL_BAUD_RATE = 115200;

/// @brief Total number of CLASSROOM EXO devices
const uint8_t NUM_DEVICES = 9;

/// @brief Minimum angle servo position in microseconds.
const uint16_t minAngleServoMicros = 2400;

/// @brief Maximum angle servo position in microseconds.
const uint16_t maxAngleServoMicros = 1265;



/** @brief Name of the device */
extern String device_name;

/** @brief Flag indicating if the device is okay */
extern bool dev_ok;

extern uint16_t current_servo_position;
extern uint16_t current_servo_micros;

/**
 * @brief Structure for messages
 */
typedef struct {
    uint8_t header;     // intended to be HEADER
    uint8_t opcode;     // intended to be one from the list above
    uint8_t dataLength; // intended to be less than MAX_DATA_LENGTH
    uint8_t data[MAX_DATA_LENGTH];
    // A little-endian system stores the least significant byte (LSB) at the lowest memory address. The “little end” (the least significant part of the data) comes first.
    // msg2send.data[0] = EMG0Average>>8u; // HIGH
    // msg2send.data[1] = EMG0Average; // LOW
    uint8_t checksum; // intended to be the sum of all received bytes
} message;


/**
 * @brief Structure for PI Controller
 */
typedef struct {
    int pwm_target;
    int pwm_current;
    int pwm_calculated;
    double current_angle;
    double setpoint_target;
    double pid_output;
    double pid_input;
    float velocity_current;
    float integral_error;
    double Kp;  // Proportional gain
    double Ki;  // Integral gain
    double Kd;
    float velocity_limit;
    float integral_limit;  // To prevent integral windup
    int deadband;  // Deadband range
    int min_pwm; // Minimum allowed PWM value
    int max_pwm; // Maximum allowed PWM value
    int min_step; // Minimum step size (twice the deadband)
} PIDController_t;


/**
 * @brief Structure for step response parameters
 */
typedef struct{
    bool active;
    unsigned long startTime;
    unsigned long maxDuration;
    int positionTolerance;
    unsigned long settleDuration;
    unsigned long withinToleranceTime;
    float initialStep;
    float finalStep;
    int currentIteration;
    int totalIterations;
    bool isInitialStep;
    bool isWaiting;
    unsigned long waitStartTime;
    unsigned long waitDuration;
} StepResponse_t;

// Signal type enumeration
enum SignalType {
    STEP,
    RAMP,
    COSINE
};

// Signal generator structure
typedef struct {
    SignalType type;
    bool active;
    unsigned long startTime;
    unsigned long maxDuration;
    unsigned long withinToleranceTime;
    float initialValue;
    float finalValue;
    int currentIteration;
    int totalIterations;
    float rampRate;
    float amplitude;
    float frequency;
    float offset;
    bool isInitialStep;
    bool rampingUp;
    bool holding;
    unsigned long holdTime;
    unsigned long holdStartTime;
    bool rampingDown;    // New state for explicit ramp down
    bool holdingLow;     // New state for holding at bottom
    
    // Added fields for step response with waiting
    bool isWaiting;
    unsigned long waitStartTime;
    unsigned long waitDuration;
    float initialStep;
    float finalStep;
} SignalGenerator_t;


// Calibration point structure
typedef struct {
    uint16_t potValue;
    uint16_t angleX10;
} CalibrationPoint;


/**
 * @brief Structure for device settings
 */
typedef struct {
    String deviceName;
    uint16_t servoZeroReferenceBytes;
    uint16_t servo110ReferenceBytes;
    uint16_t servoZeroReferenceDegrees;
    uint16_t servo110ReferenceDegrees;
    int servoZeroReferenceMicros;
    int servo110ReferenceMicros;
    uint16_t forceZeroReferenceValue;
    CalibrationPoint servoCalibration[NUM_CALIBRATION_POINTS];
} DeviceSettings;

const DeviceSettings deviceSettingsArray[] = {
    // deviceName, servoZeroReferenceBytes, servo110ReferenceBytes, servoZeroReferenceDegrees, servo110ReferenceDegrees, servoZeroReferenceMicros, servo110ReferenceMicros, forceZeroReferenceValue
    {"01_CLASSROOM_EDU_EXO_PRO", 499, 2478, 1800, 700, 2400, 1265, 1495, {  
        {499, 1800},   // 180.0°
        {671, 1700},   // 170.0°
        {855, 1600},   // 160.0°
        {1026, 1500},   // 150.0°
        {1212, 1400},  // 140.0°
        {1384, 1300},  // 130.0°
        {1562, 1200},  // 120.0°
        {1747, 1100},  // 110.0°
        {1925, 1000},  // 100.0°
        {2115, 900},   // 90.0°
        {2291, 800},   // 80.0°
        {2478, 700}    // 70.0°
    }}, 
    {"02_CLASSROOM_EDU_EXO_PRO", 464, 2438, 1800, 700, 2400, 1265, 1500, { 
        {471, 1800},   // 180.0°
        {633, 1700},   // 170.0°
        {833, 1600},   // 160.0°
        {1007, 1500},   // 150.0°
        {1176, 1400},  // 140.0°
        {1377, 1300},  // 130.0°
        {1573, 1200},  // 120.0°
        {1755, 1100},  // 110.0°
        {1907, 1000},  // 100.0°
        {2082, 900},   // 90.0°
        {2277, 800},   // 80.0°
        {2438, 700}    // 70.0°
  }}, 
    {"03_CLASSROOM_EDU_EXO_PRO", 457, 2462, 1800, 700, 2296, 1059, 1470, { 
        {457, 1800},   // 180.0°
        {633, 1700},   // 170.0°
        {817, 1600},   // 160.0°
        {1004, 1500},   // 150.0°
        {1192, 1400},  // 140.0°
        {1367, 1300},  // 130.0°
        {1550, 1200},  // 120.0°
        {1742, 1100},  // 110.0°
        {1923, 1000},  // 100.0°
        {2096, 900},   // 90.0°
        {2281, 800},   // 80.0°
        {2462, 700}    // 70.0°
    }},
    {"04_CLASSROOM_EDU_EXO_PRO", 501, 2465, 1800, 700, 2400, 1265, 1470, { 
        {501, 1800},   // 180.0°
        {655, 1700},   // 170.0°
        {836, 1600},   // 160.0°
        {1009, 1500},   // 150.0°
        {1200, 1400},  // 140.0°
        {1374, 1300},  // 130.0°
        {1553, 1200},  // 120.0°
        {1749, 1100},  // 110.0°
        {1928, 1000},  // 100.0°
        {2093, 900},   // 90.0°
        {2297, 800},   // 80.0°
        {2465, 700}    // 70.0°
    }},
    {"05_CLASSROOM_EDU_EXO_PRO", 863, 308, 1800, 700, 2296, 1059, 1500, { // not true!
        {3621, 1800},   // 180.0°
        {3429, 1700},   // 170.0°
        {3250, 1600},   // 160.0°
        {3062, 1500},   // 150.0°
        {2893, 1400},  // 140.0°
        {2705, 1300},  // 130.0°
        {2532, 1200},  // 120.0°
        {2337, 1100},  // 110.0°
        {2147, 1000},  // 100.0°
        {1970, 900},   // 90.0°
        {1792, 800},   // 80.0°
        {1616, 700}    // 70.0°
    }}, // not true!
    {"06_CLASSROOM_EDU_EXO_PRO", 436, 2451, 1800, 700, 2400, 1265, 1370, { 
        {436, 1800},   // 180.0°
        {636, 1700},   // 170.0°
        {807, 1600},   // 160.0°
        {995, 1500},   // 150.0°
        {1172, 1400},  // 140.0°
        {1355, 1300},  // 130.0°
        {1523, 1200},  // 120.0°
        {1699, 1100},  // 110.0°
        {1886, 1000},  // 100.0°
        {2077, 900},   // 90.0°
        {2263, 800},   // 80.0°
        {2451, 700}    // 70.0°
    }},
    {"07_CLASSROOM_EDU_EXO_PRO", 461, 2460, 1800, 700, 2400, 1265, 1406, { 
        {455, 1800},   // 180.0°
        {637, 1700},   // 170.0°
        {820, 1600},   // 160.0°
        {993, 1500},   // 150.0°
        {1174, 1400},  // 140.0°
        {1344, 1300},  // 130.0°
        {1541, 1200},  // 120.0°
        {1722, 1100},  // 110.0°
        {1899, 1000},  // 100.0°
        {2083, 900},   // 90.0°
        {2267, 800},   // 80.0°
        {2457, 700}    // 70.0°
    }},
    {"08_CLASSROOM_EDU_EXO_PRO", 486, 2458, 1800, 700, 2400, 1265, 1700, { 
        {486, 1800},   // 180.0°
        {653, 1700},   // 170.0°
        {841, 1600},   // 160.0°
        {1004, 1500},   // 150.0°
        {1198, 1400},  // 140.0°
        {1383, 1300},  // 130.0°
        {1566, 1200},  // 120.0°
        {1733, 1100},  // 110.0°
        {1910, 1000},  // 100.0°
        {2102, 900},   // 90.0°
        {2277, 800},   // 80.0°
        {2458, 700}    // 70.0°
    }}, 
    {"ESP32-BT-Slave", 1000, 1000, 1000, 1000, 1000, 1000, 1400, {
        {100, 1800},   // 180.0°
        {200, 1700},   // 170.0°
        {300, 1600},   // 160.0°
        {400, 1500},   // 150.0°
        {500, 1400},  // 140.0°
        {600, 1300},  // 130.0°
        {700, 1200},  // 120.0°
        {800, 1100},  // 110.0°
        {900, 1000},  // 100.0°
        {1000, 900},   // 90.0°
        {1100, 800},   // 80.0°
        {1200, 700}    // 70.0°
    }}};


/** @brief Global instance of message to send */
extern message msg2send;

/** @brief Global instance of message to receive */
extern message msg2receive;

/** @brief Global instance of current device settings */
extern DeviceSettings currentSettings;

/** @brief Global instance of current device settings */
extern PIDController_t servo_controller;

extern StepResponse_t step_response;

// Global variables
extern SignalGenerator_t signalGen;  // Declaration of global variable

/** 
 * @brief Initialize the basic hardware components. 
 */
void initializeHardware();

/**
 * @brief Finds device settings based on the given name
 * 
 * @param name The name of the device settings to find
 * @param settings Reference to a DeviceSettings object where the found settings will be stored
 * @return true If the settings were found successfully, false otherwise
 */
bool findDeviceSettings(const String& name, DeviceSettings *settings);

/**
 * @brief Checks the name of the device, and saves default values accordingly
 */
void checkDeviceIntegrity();
#endif // CONFIG_H

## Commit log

2023-11-08 CAD for Github LRS
    [EDUEXO-custom-PCB-B_Cu.gbr, EDUEXO-custom-PCB-B_Mask.gbr, EDUEXO-custom-PCB-B_Paste.gbr, EDUEXO-custom-PCB-B_Silkscreen.gbr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]
2023-11-08 PCB GUI and force/EMG control
2023-11-30 Delete 1_CAD_File/Shoulder 0.6 nozzle.stl
    Not needed
    [Shoulder 0.6 nozzle.stl]
2023-12-09 Open-Source Material for Scientific Paper
    [EDUEXO-custom-PCB-B_Cu.gbr, EDUEXO-custom-PCB-B_Mask.gbr, EDUEXO-custom-PCB-B_Paste.gbr, EDUEXO-custom-PCB-B_Silkscreen.gbr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]
2024-10-14 Classroom Exo Arduino Code
2024-10-14 Updated Matlab GUI
    [arm.stl, arm_.stl, head.stl, torso.stl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]
2024-10-14 fixed Pin select
2025-01-20 Commit Changes Nov 2024
    [EduExo_LowerArm v1.stl, EduExo_UpperArm v2.stl]
2025-01-20 Supplementary Materials
    [Cuff_v2.stl, Myoware 1.0_Case_V1-letters.stl, Myoware_1.0_Case_V1.stl, Wrist_Cuff_v2.stl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]
